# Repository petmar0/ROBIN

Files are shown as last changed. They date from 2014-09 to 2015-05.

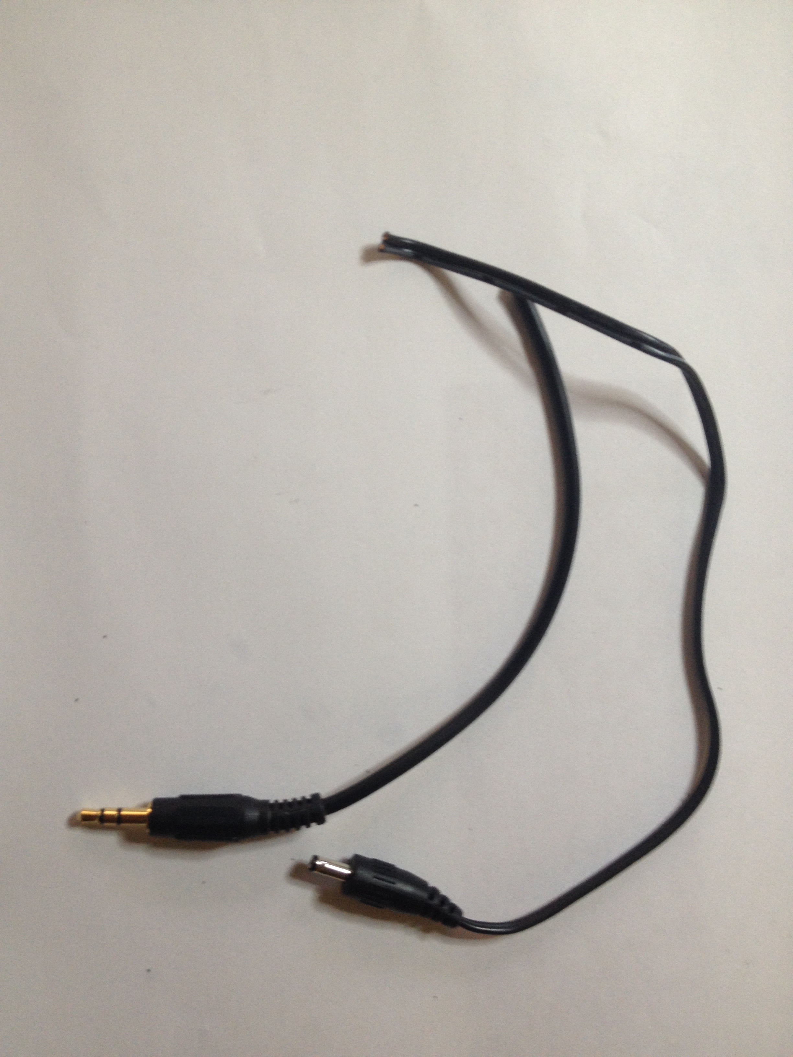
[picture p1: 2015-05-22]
IMG_1970.jpg

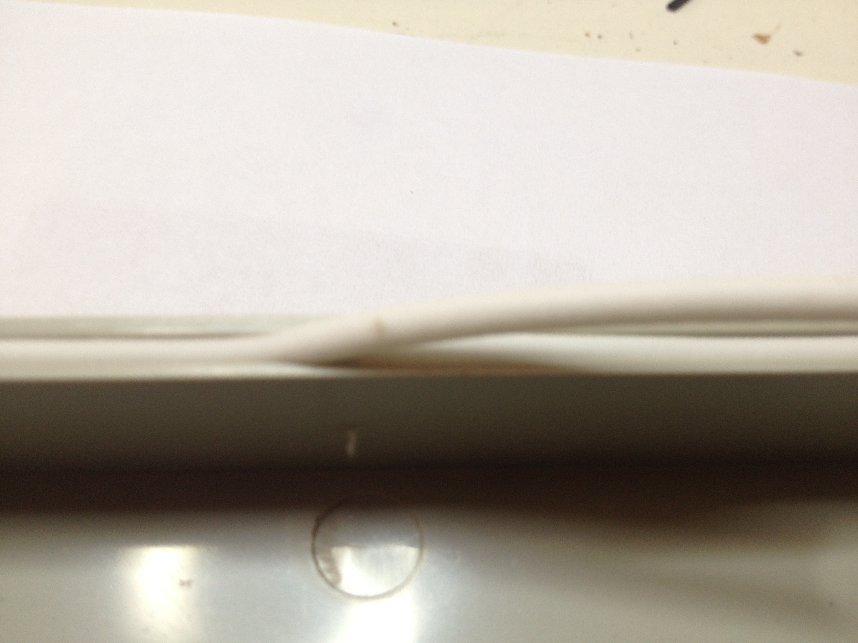
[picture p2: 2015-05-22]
IMG_1957.jpg

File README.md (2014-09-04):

ROBIN
=====
###Recording and Observing Bioacoustic Identifying Node
The basic idea of this system is two-fold: to create a device that will allow for individuals interested in the detection and identification of birds on a citizen science level to assemble their own unit and use it, and to develop the software to be used on this system to do the detection and classification of organisms by signal characteristics. To accomplish this, the system must have several characteristics. It must be:
- Inexpensive (<$200)
- Modular, such that parts that are preexisting may be used
- Open-source, to allow for collaborative improvements
- Fully supported, both on the engineering and biological sides, to answer users’ questions
- Easy to assemble
- Easy to initialize
- Easy to use

Additionally, from the scientific standpoint, several other features should be included for use in the field:
- Low-power, i.e. capable of being powered by a single 10 W solar panel and battery
- Weatherproof, i.e. IP67 rated or better and capable of operation from -20 to 50 °C
- Remotely accessible for data, i.e. accessible via cellular modem

This makes it possible to create two or more models of the device. In the simplest version, a user who wishes to identify birds at their bird feeders will string a microphone out through a window, install the software on an old laptop, and run this with the screen off, pushing data to a centralized database on a server at CLO. In the more advanced embodiment, a scientist wishing to record night flight calls of various passerines will have a single-board computer sealed in a box with a cellular modem, and connected to at least one microphone outside the enclosure via a waterproof connector.
In the two aforementioned scenarios, each unit is tailored to its application in the hardware domain, keeping hardware costs as low as possible. In the meantime, this adaptable hardware may be coupled with the same software in both cases to run near-realtime detection and report classified detections back to a centralized database.

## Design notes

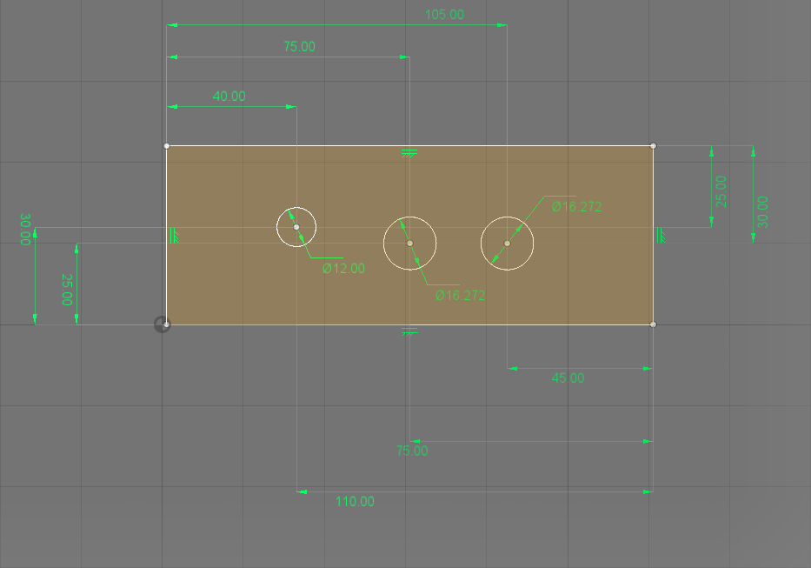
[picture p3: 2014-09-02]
Hole Pattern for End.png

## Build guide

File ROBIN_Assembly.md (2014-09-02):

#Recording and Observing Bioacoustic Identifying Node: Assembly
##Tools Needed
- No. 1 Phillips Screwdriver
- 41/64" Drill Bit
- No. 30 Drill Bit
- 12 mm Drill Bit
- Drill
- Wire Cutter
- Wire Stripper
- Adjustable Wrench
- The computer that you're reading this on
- SD Card Reader
- Soldering Iron with Solder
- Multimeter

##Parts Needed
###Node
- 1x [Enclosure](http://www.amazon.com/dp/B00HG8TS3Y/ref=wl_it_dp_o_pC_S_ttl?_encoding=UTF8&colid=H2U0Y6WJ23VC&coliid=I2G3479UF6VSP0)
- 1x [Female 3-pin EN3 Connector](http://www.alliedelec.com/search/productdetail.aspx?SKU=70214361)
- 1x [Male 2-pin EN3 Connector](http://www.alliedelec.com/search/productdetail.aspx?SKU=70214332)
- 1x [Female 2-pin EN3 Connector](http://www.alliedelec.com/search/productdetail.aspx?SKU=70214365)
- 1x [Syba Audio Interface](http://www.amazon.com/Syba-SD-CM-UAUD-Adapter-C-Media-Chipset/dp/B001MSS6CS/ref=sr_1_1?s=electronics&ie=UTF8&qid=1408040850&sr=1-1&keywords=usb+audio+adapter)
- 1x [Raspberry Pi Model B](http://www.amazon.com/RASPBERRY-MODEL-756-8308-Raspberry-Pi/dp/B009SQQF9C/ref=sr_1_1?ie=UTF8&qid=1408473974&sr=8-1&keywords=raspberry+pi+model+b)
- 1x [Powered USB Hub](http://www.amazon.com/Belkin-Aluminium-Powered-Adapter-Desktop/dp/B00K8AB1MI/ref=sr_1_1?ie=UTF8&qid=1408463292&sr=8-1&keywords=powered+usb+hub)
- 1x [Wi-Pi WiFi Dongle](http://www.amazon.com/Wi-Pi-Raspberry-802-11n-Wireless-Adapter/dp/B00BDW6D7I/ref=sr_1_15?ie=UTF8&qid=1408473936&sr=8-15&keywords=raspberry+pi+model+b+wifi+power)
- 1x [USB A to microB Cable](http://www.amazon.com/StarTech-com-Micro-USB-Cable-UUSBHAUB3RA/dp/B001AR4NC8/ref=sr_1_2?ie=UTF8&qid=undefined&sr=8-2&keywords=short+usb+micro+B+right+angle)
- 1x [USB A to miniB Cable](http://www.amazon.com/StarTech-1-Feet-Mini-USB-Cable/dp/B002L5U7N2/ref=sr_1_4?ie=UTF8&qid=1408466830&sr=8-4&keywords=1ft+usb+mini+B)
- 1x [16 GB SD Card](http://www.amazon.com/gp/product/B009QZH7D8)
- 1x [LM7805 Voltage Regulator](http://www.amazon.com/Through-Positive-Voltage-Regulator-L7805CV/dp/B00CMQ4NYO/ref=sr_1_2?ie=UTF8&qid=1409319128&sr=8-2&keywords=7805)
- 1x [Power Supply](http://www.amazon.com/Hitlights-110VAC-12VDC-Adapter-Transformer/dp/B007ME2HMQ/ref=sr_1_1?ie=UTF8&qid=1409319084&sr=8-1&keywords=12+vdc+transformer)
- 1x [12"x12"x3/16" Piece of Plastic](http://www.amazon.com/dp/B0070Z651Q/ref=biss_dp_t_asn)
- 4x [#6x3/8" Sheet Metal Screws](http://www.amazon.com/Sheet-Metal-Screw-Phillips-Stainless/dp/B00JXV4UP8/ref=sr_1_2?ie=UTF8&qid=undefined&sr=8-2&keywords=6x3%2F8+sheet+metal+screw)
- 1x [Desiccant Block](http://www.amazon.com/Dry-Brik-II-Desiccant-Blocks-6-Pack/dp/B000U0XCZA/ref=sr_1_2?ie=UTF8&qid=1409320779&sr=8-2&keywords=disposable+desiccant)
- 1x [Velcro Pack](http://www.amazon.com/Velcro-brand-Mini-Fasteners-White/dp/B00A2GMCE4/ref=sr_1_1?ie=UTF8&qid=1409320839&sr=8-1&keywords=velcro+dots)
- 1x [Pressure Compensation Element](http://www.sealingdevices.com/gore-vents)
- 4x [1/8" Zip Ties](http://www.amazon.com/Zip-Ties-inch-Qty-000/dp/B00BVFQD18/ref=sr_1_13?ie=UTF8&qid=1409321447&sr=8-13&keywords=1%2F8%22+zip+tie)
- 4x [4-40 x 3/8" Nylon Screws](http://www.amazon.com/dp/B000N8STWK/ref=biss_dp_t_asn)
- 2x [4-40 x 1/2" Nylon Standoffs](http://www.amazon.com/Richco-HTS4-8-48-Standoff-thread-length/dp/B00LPPP1Y4/ref=sr_1_5?ie=UTF8&qid=1409321793&sr=8-5&keywords=nylon+4-40+standoff)

###Microphone
- 1x [Microphone Element](http://www.jlielectronics.com/products/JLI%252d61A.html)
- 2x [Male 3-pin EN3 Connector](http://www.alliedelec.com/search/productdetail.aspx?SKU=70214349)
- 1x [Male 3-pin EN3 Connector](http://www.alliedelec.com/search/productdetail.aspx?SKU=70214349)
- 1x [Female 3-pin Cable End EN3 Connector](http://www.alliedelec.com/search/productdetail.aspx?SKU=70214377)
- 1x [Spacer 1](http://www.mcmaster.com/#95606A430)
- 1x [Spacer 2](http://www.mcmaster.com/#94639a155)
- 1x [Sleeve 1](http://www.mcmaster.com/#6627K13)
- 1x [Sleeve 2](http://www.mcmaster.com/#6621K75)
- 1x [Bearing](http://www.mcmaster.com/#6362K233)
- 1x [Gore-Tex® Acoustic Membrane](http://www.gore.com/en_xx/products/venting/portable/cell-phone-product-comparison.html?isAjax=true)
- 1x [Tube of Intertex UV-6800](http://www.amazon.com/E-6000-260011-UV6800®-3-7-Adhesive/dp/B004JX3C2C)
- 1x [15' Microphone Extension Cable](http://www.amazon.com/3-5mm-Stereo-Headphone-Extension-Straight/dp/B0002KR13M/ref=sr_1_14?ie=UTF8&qid=1408040298&sr=8-14&keywords=long+microphone+cables)

##Assembly
###Node
1. Begin by cutting out the pattern found here from the piece of plastic
2. Drill out the 1/8" holes
3. Attach the USB hub to the four holes in the bottom right corner with four zip ties with the ports facing right and up
4. Attach the standoffs to the plastic using two 4-40 screws in the holes in the top center
5. Attach the Raspberry Pi to the standoffs using the other two 4-40 screws
6. Plug the USB A to miniB cable into a USB port on the Raspberry Pi
7. Plug the other end of the USB A to miniB cable into the top of the USB hub
8. Plug the USB to microB cable into the microB connector on the Raspberry Pi
9. Plug the other end of the USB A to microB cable into the right side of the USB hub
10. Plug the Syba Audio Interface into the USB hub
11. Plug the Wi-Pi WiFi Dongle into the USB hub
12. Drill the two holes in the bottom wall of the enclosure for the external connectors with the pattern found here and the 41/64" drill bit
13. Drill the one remaining hole in the bottom wall with the 12 mm drill bit
14. Put the pressure relief element in from the outside of the enclosure
15. Screw the included nut on the pressure relief element from the inside
13. Cut off 1' of the USB hub power cord from the connector
14. Separate and strip the ends of both of the wires of the USB hub power cord that was just cut
15. Tin the wire ends with solder
16. Solder the middle pin (pin 2) of the LM7805 to the pin on the 2-pin EN3 female panel connector with the small dot next to it (pin 1)
17. Solder the left pin (pin 1) of the LM7805 to the other pin on the panel connector
18. Check which conductor of the power cable connects to the outside of the barrel conenctor using the multimeter in continuity or resistance mode
19. Solder that conductor to the middle pin of the LM7805
20. Solder the other conductor to the empty pin (pin3) of the LM7805
21. Cut off a foot of cable including the male 3.5 mm plug from the microphone extension cable
22. Solder the bare conductor to the pin with the dot next to it (pin1)
23. Solder the red wire to the pin across the notch from pin 1 (pin2)
24. Solder the black wire to the remaining pin below the other two (pin3)
25. Put the 3-pin EN3 connector through the hole near the middle of the bottom
26. Screw the included nut onto the 3-pin EN3 connector
27. Put the 2-pin EN3 connector through the hole at the right side of the bottom
28. Screw the included nut onto the 2-pin EN3 connector
32.

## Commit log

2014-09-02 Initial Commits
    [Hole Pattern for End.f3d, Plate.f3d, Plate.stl]
2015-05-22 Added Assembly Pics
